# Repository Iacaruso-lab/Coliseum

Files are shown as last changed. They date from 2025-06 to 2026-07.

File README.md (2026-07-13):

# Coliseum

Hemispherical display to deliver simultaneous auditory and visual stimuli to head-fixed rodents. The device is composed by 15 slices.

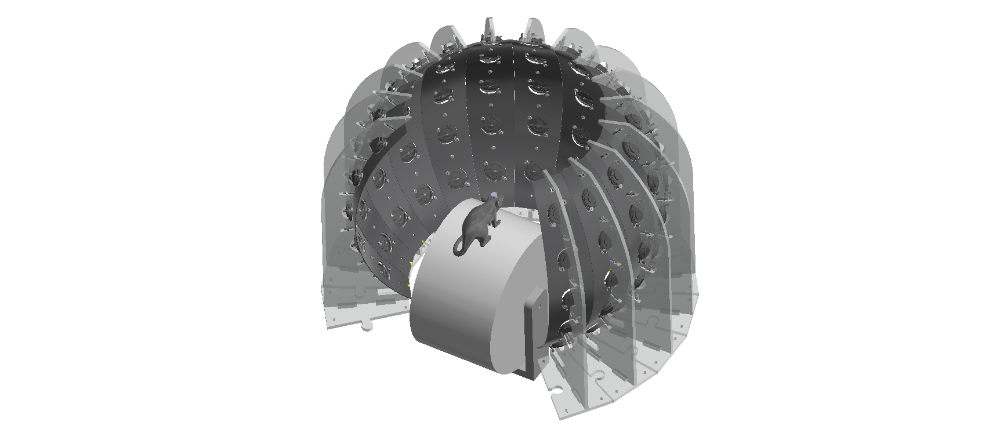
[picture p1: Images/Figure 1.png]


The device is designed to receive messages sent from the computer serial port, each message will contain digital information for each slide, basically which LED and which speaker goes into "ON state".

The audio signal is continuously generated from the PC and sent to all speakers but only the speakers set to ON will play the auditory signals.

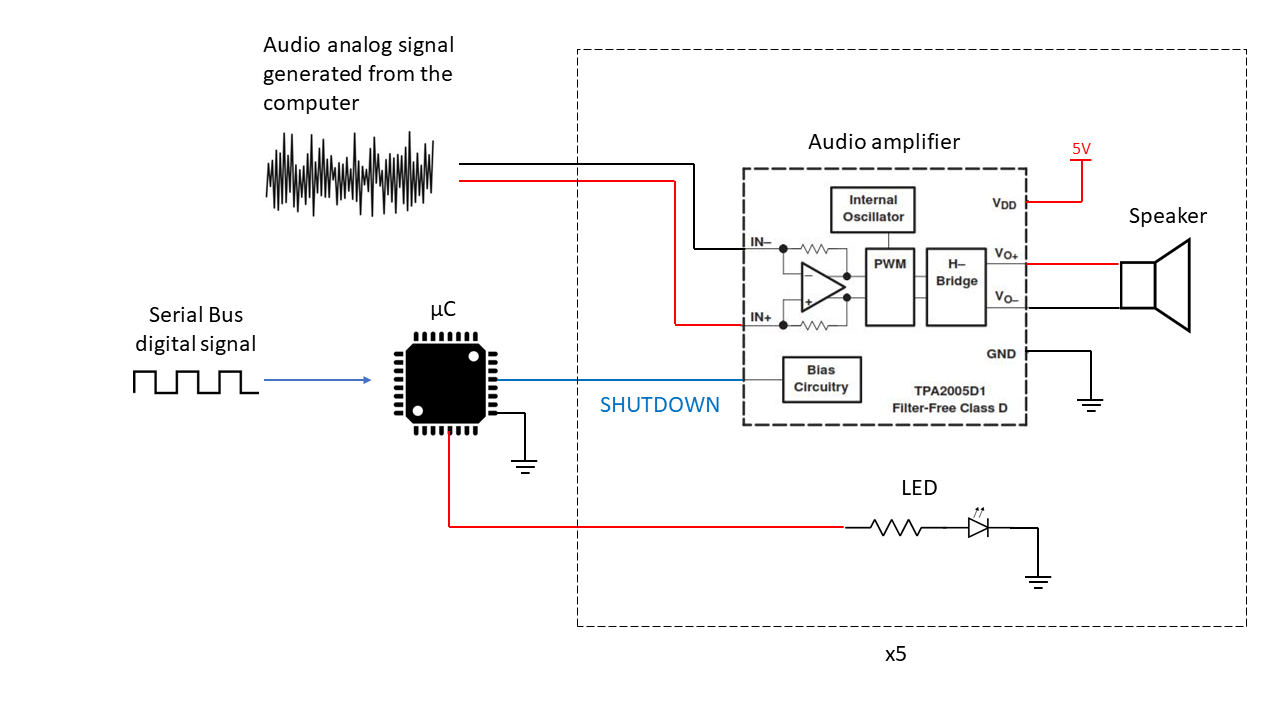
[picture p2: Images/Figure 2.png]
working principle


## Bill of materials

## Ordering the PCBs

First you need to create a customer account with [JLCPCB](https://jlcpcb.com/).

Then drag the gerber file from the [slice manufacturing files folder](Hardware/Manufacturing%20files/Slice%20PCB) into the instant quote file upload window.

Then select ***PCB quantity 15, PCB thickness 0.8 and color black.***

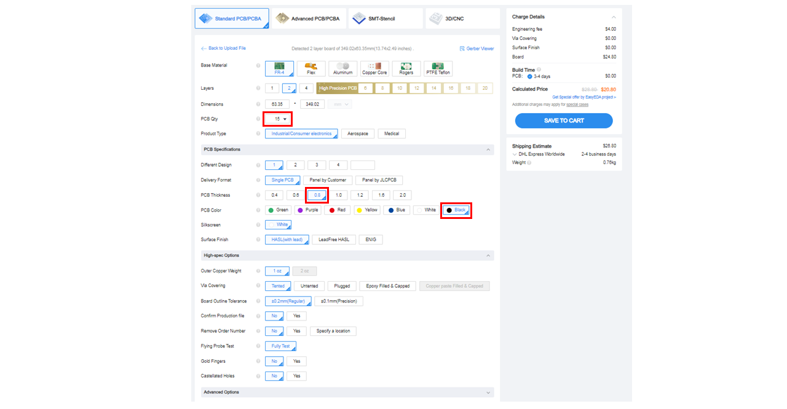
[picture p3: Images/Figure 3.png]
PCB order 1


Select PCB assembly and leave the selection of the top side for the assembly of the LEDs. Then select next.

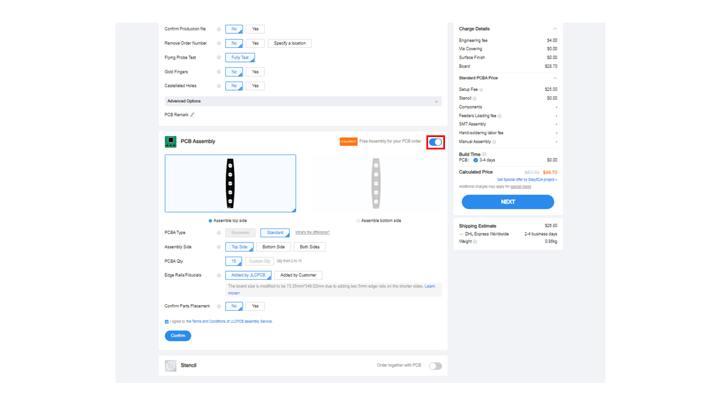
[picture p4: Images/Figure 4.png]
PCB order 2


Select next on the following step.

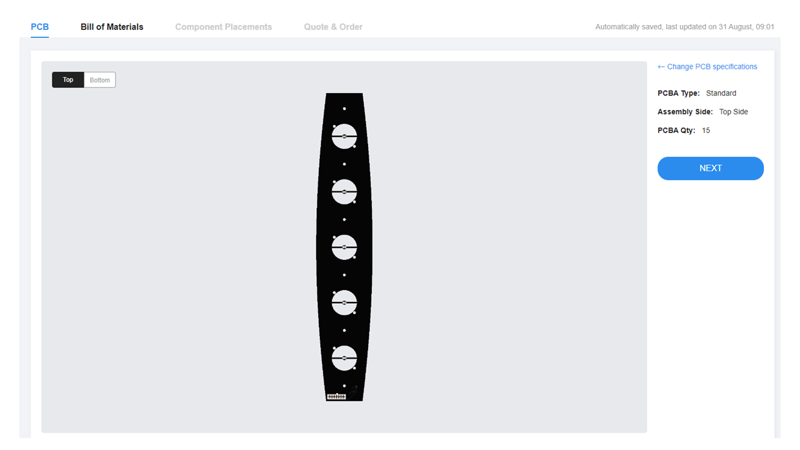
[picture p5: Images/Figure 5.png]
PCB order 3


After that wou are asked to upload the [BOM and Pick and Place files](Hardware/Manufacturing%20files/Slice%20PCB) then click on next.

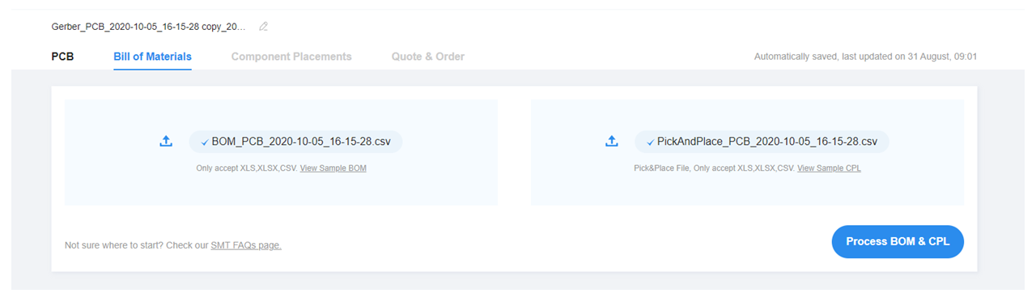
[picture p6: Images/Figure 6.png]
PCB order 4


On the following step you can select which components from the bill of materials you uploaded you want to be asembled on the board, when we ordered them there was no stock of the header, if there is, please ***unselect H1. Just leave selected the LEDs, coloured in red on the caption.***

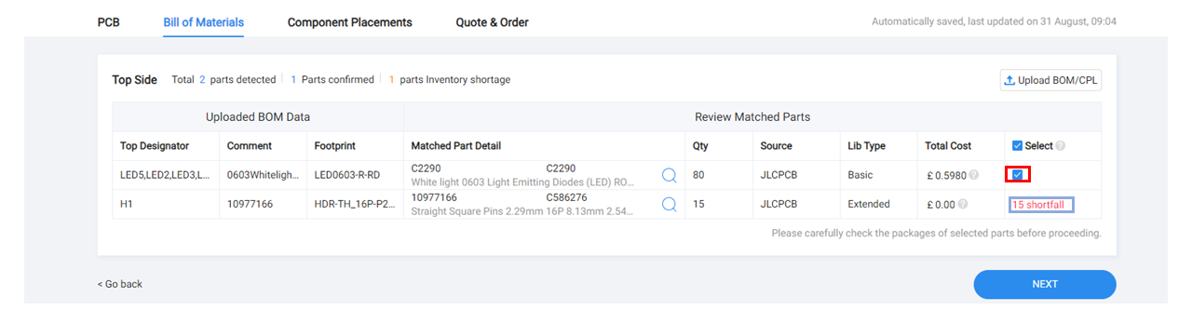
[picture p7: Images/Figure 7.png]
PCB order 5


After clicking on next you will get a message informing that your project has unselected parts, just click on ***"do not place"*** option.

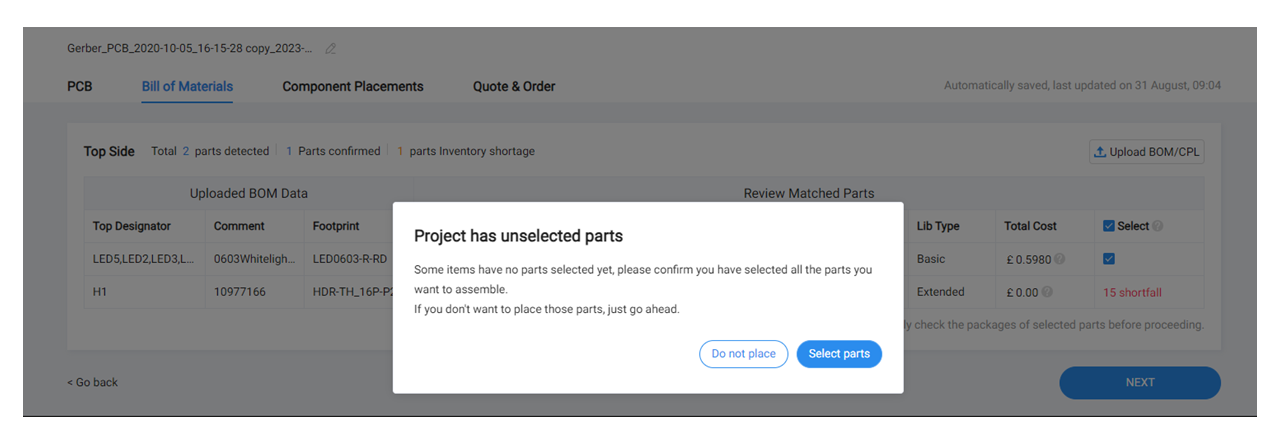
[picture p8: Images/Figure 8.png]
PCB order 6


On the render you ***should not see any part on top of the bottom header H1***, if you zoom in you will be able to see the LEDs in place where they will be once you receive the PCBs. Then you can click next.

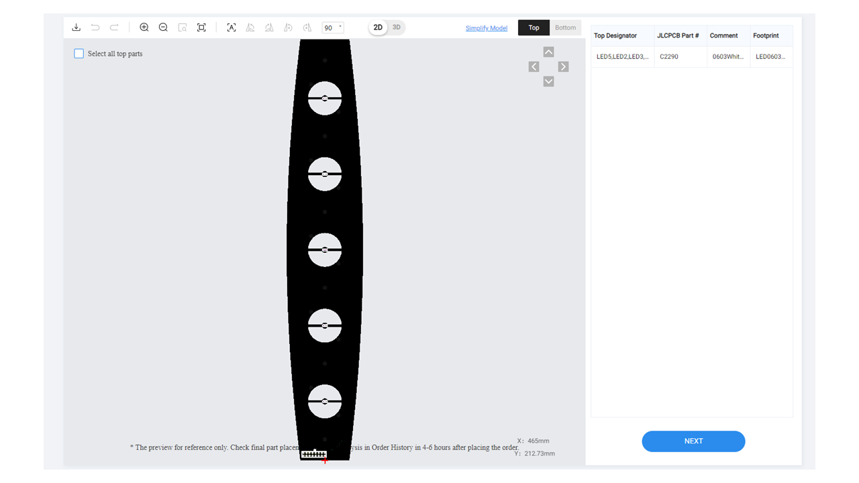
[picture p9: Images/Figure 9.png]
PCB order 7


On the last window you can just save the order for further payment.

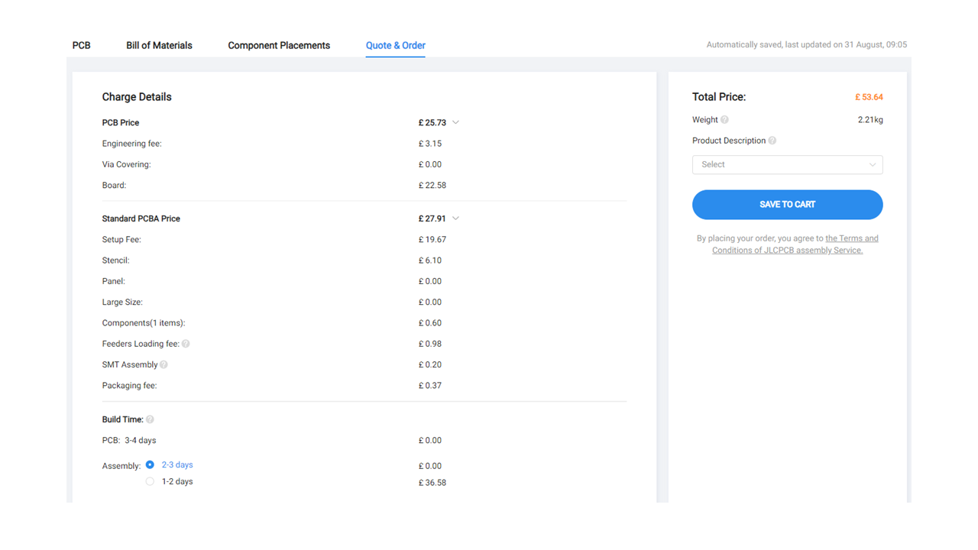
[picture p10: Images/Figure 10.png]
PCB order 8


The same steps have to be repeated for the [control board](Hardware/Manufacturing%20files/Control%20PCB/V7) manufacturing files, in that case ***the colour does not mater and can be the default greeen as well as the PCB thickness which can be the standard 1.6 mm***, the number of units is still 15.

## Assembly instructions

### Slice assembly

1- Laser cut the 15 slices acrylic structure. The ai. file "4 Slices Laser cutting file" contained in [the laser cut files folder](Hardware/Manufacturing%20files/Laser%20cut) has the 5 mm acrylic PMMA components needed for the main structure. Our file has been generated for a 600 mm x 300 mm laser cutter bed.

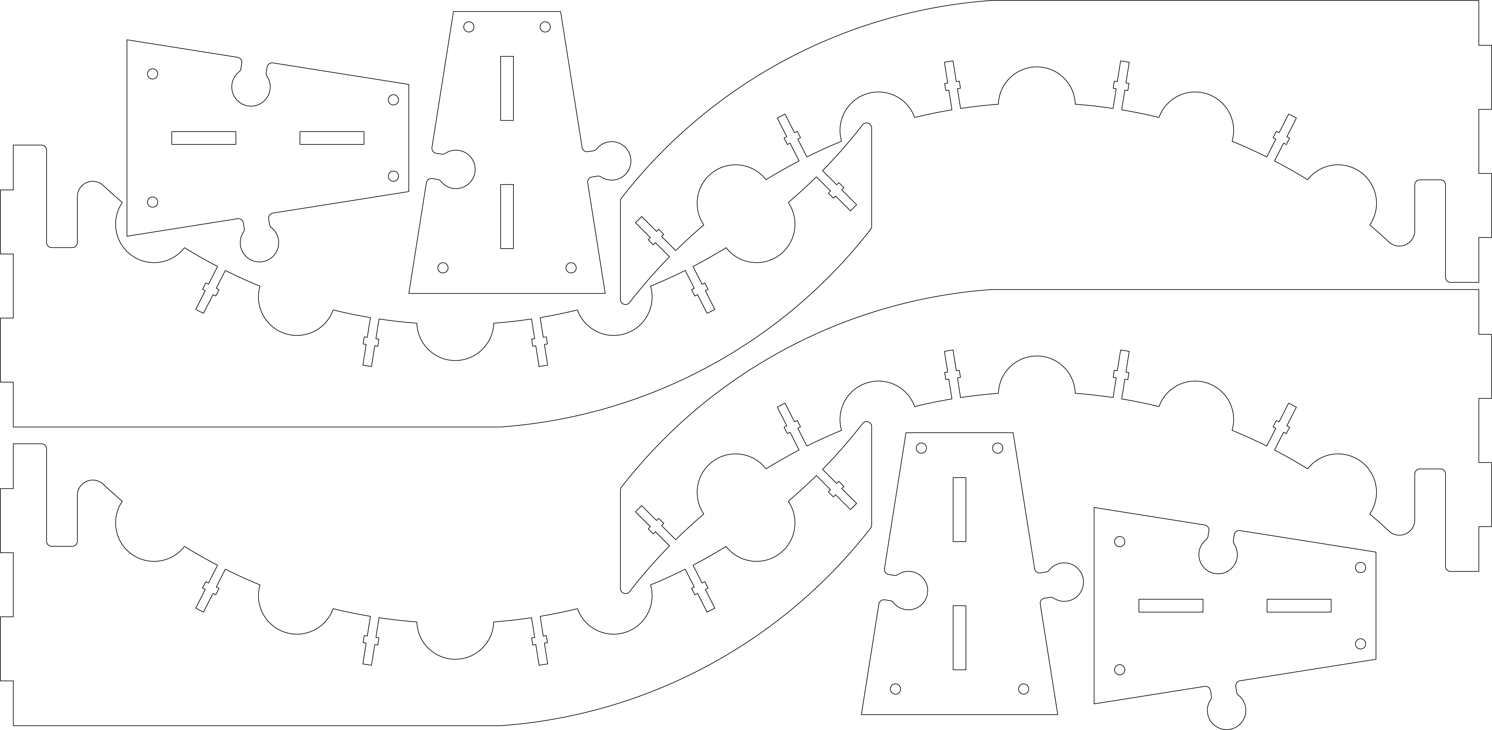
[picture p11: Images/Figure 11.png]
4 Slices (Laser cutting file)


Then both components of the acrylic structure are glued together, in our case we appyed the [Dymax UV curing glue](https://dymax.com/products/equipment/light-curing-equipment/spot-curing-systems) in the intersection of both parts, this step has to be repeated for each slide.

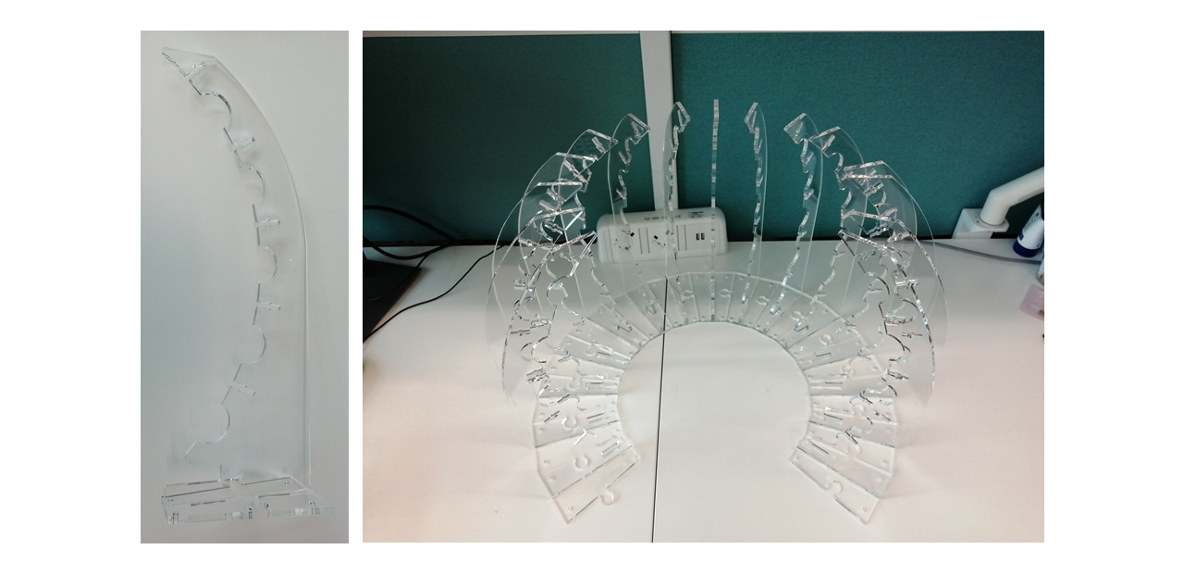
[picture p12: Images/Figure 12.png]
acrylic


The third component is the spacer which needs to be cut using 2 mm thick acrylic. You are going to need 150 spacers, a couple for each speaker. They will create the minimum space needed between the speaker membrane and the PCB avoiding the transfer of sound vibrations.

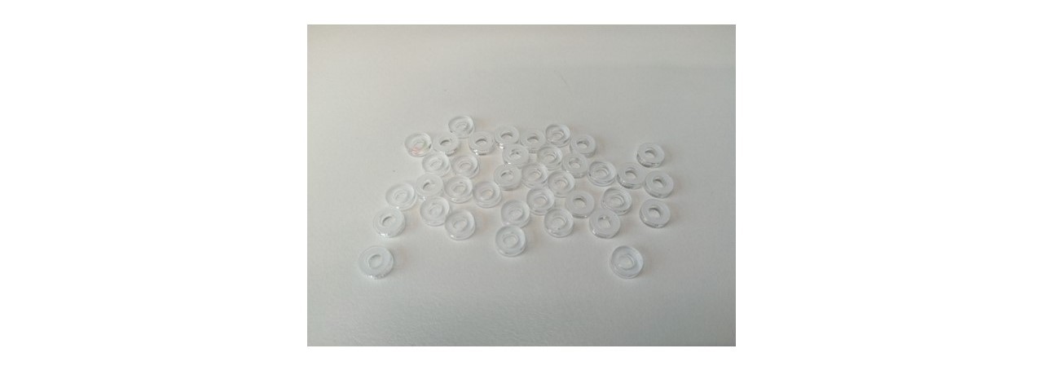
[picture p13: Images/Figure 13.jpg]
spacer


Each of the [speakers](https://www.digikey.co.uk/en/products/detail/visaton-gmbh-co-kg/K-28-WPC-BL-8-OHM/9842354) is attached with the PCB using 2 spacers, [2 M3 x 12 mm screws](https://www.amazon.co.uk/gp/product/B09Q5YYVQ2/ref=ppx_yo_dt_b_asin_title_o01_s00?ie=UTF8&psc=1) and two [M3 nuts](https://www.amazon.co.uk/TERF-Hexagon-Steel-Full-Nuts/dp/B09MDJHJTB/ref=sr_1_6?crid=2JZVZ1J4DZOUH&keywords=M3%2Bnuts&qid=1693322964&sprefix=m3%2Bnuts%2Caps%2C63&sr=8-6&th=1). Then all the Speakers are soldered using single core wire. The wire is cut at approximately 15 mm lengh and both sides stripped with a cable stripping tool.

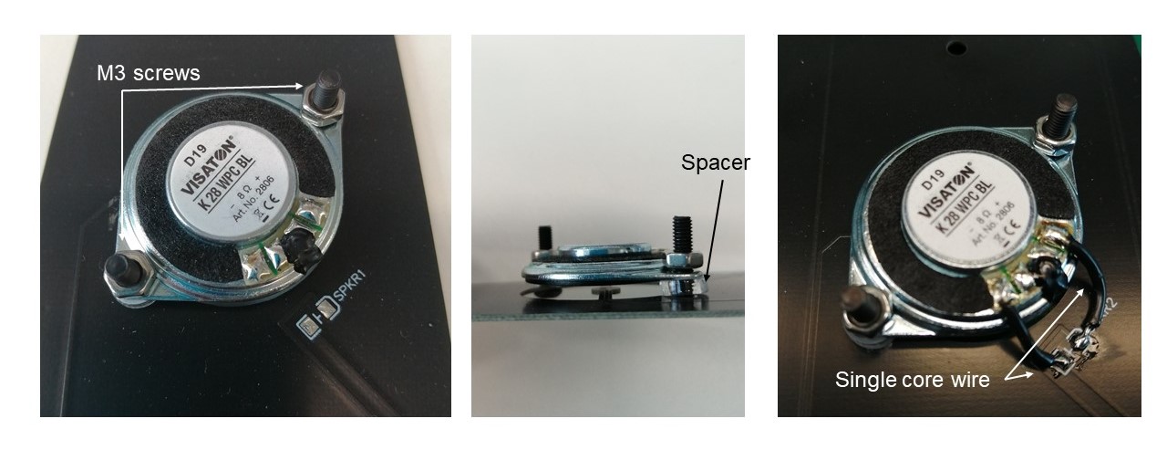
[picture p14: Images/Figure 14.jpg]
figures


The assembly of each slice PCB with its structure is done by using five M3 x 16 mm screws and five M3 nuts:

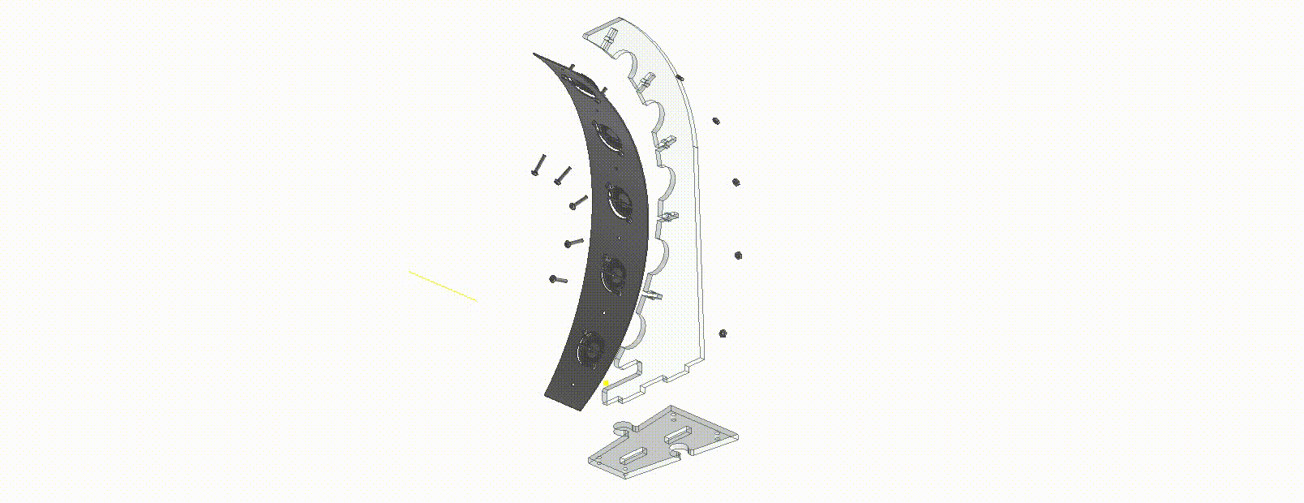
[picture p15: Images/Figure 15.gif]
Assembly


Once the slice is assembled, the last step is to bent the pins of the [8x2 female header](https://uk.farnell.com/samtec/esq-108-14-g-d/connector-rcpt-16pos-2row-2-54mm/dp/2779427) approximately 30 degrees using a ruler and solder the header into the back side of the PCB.

Slice assembly

Once you have repeated the process for all 15 slices you get this.

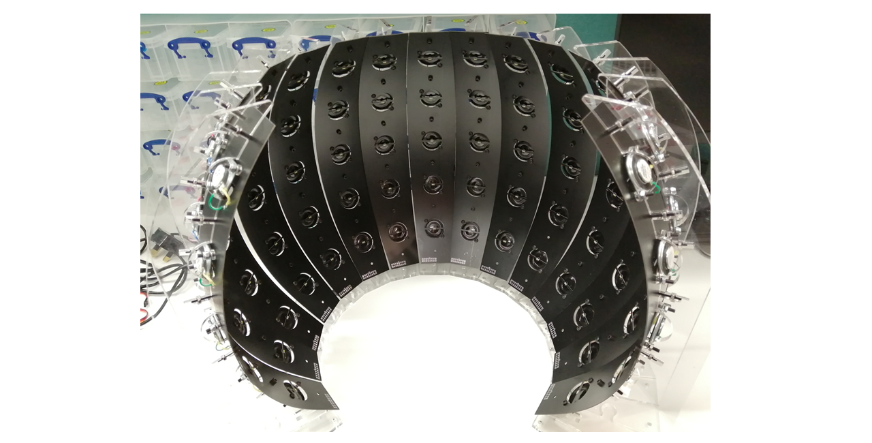
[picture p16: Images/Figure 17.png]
Coliseum assembled


### Control board assembly

If all components are in stock on [JLCPCB](https://jlcpcb.com/) the boards should arrive fully assembled and the only assembly step is the connection between its 90 degree connector and the slice connector.

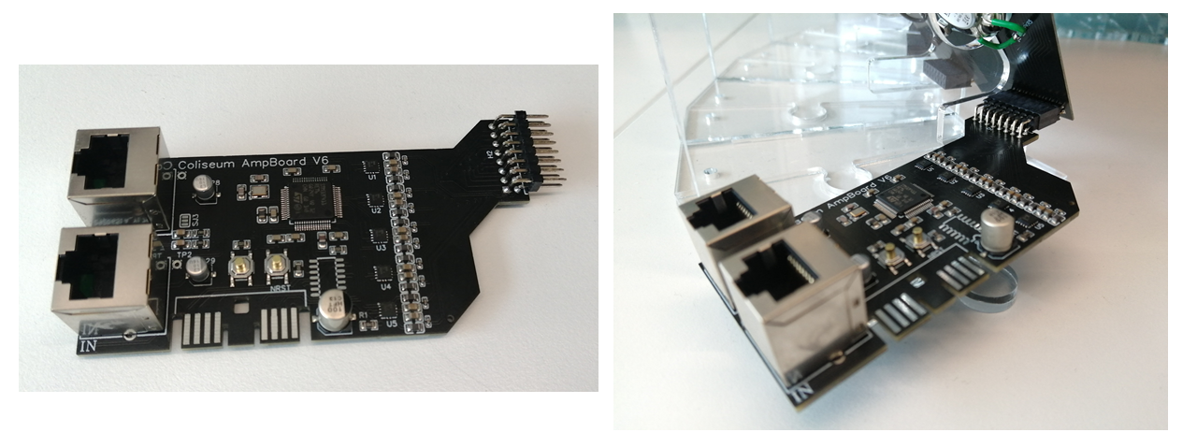
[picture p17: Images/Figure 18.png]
Coliseum board


### Programmer board assembly

The "georgeous STM32 programmer" board is composed by a custom PCB that is soldered on top of the [STM32 Nucleo-64 MCU Development Board NUCLEO-F410RB](https://uk.rs-online.com/web/p/microcontroller-development-tools/9173766?cm_mmc=UK-PPC-DS3A-_-google-_-3_UK_EN_Raspberry+Pi+%26+Arduino+%26+ROCK+%26+STEM+Education+%26+Development+Tools_Microcontroller+Development+Tools-_-STMicroelectronics+-+9173766+-+NUCLEO-_-stmicroelectronics+nucleo&matchtype=p&aud-2406926037817:kwd-327069370714&cq_src=google_ads&cq_cmp=12690202697&cq_term=stmicroelectronics%20nucleo&cq_plac=&cq_net=g&cq_plt=gp&gclsrc=aw.ds&gad_source=1&gad_campaignid=12690202697&gbraid=0AAAAADkeWNOcTAzA5nZgKzR7_I_gj5hWe&gclid=CjwKCAjwmdLSBhANEiwAkREMN9kaxucJEJcilK4NKpdcp2L4rGTd5La0k6RWjJVKPHo56LOtS3Y6xBoCotoQAvD_BwE) Serial to USB converter part that can snap and be separated from the rest of the development board.
Vcc, SWDIO, GND, SWCLK, NRST, RX and TX pins are soldered with a [Molex EdgeLock connector](https://www.mouser.co.uk/en/ProductDetail/Molex/200890-0106?qs=W0yvOO0ixfHAR9KO0O7TGQ%3D%3D) using a ribbon cable.

### If there is no stock of LEDs in JLCBPCB and you need to solder them my hand

The LEDs can be ordered to [RS components](https://uk.rs-online.com/web/p/leds/6541800).

You will have to check the polarity of each LED using a multimiter in the diode position. The position of the black and red probes will indicate the right polarity of the LED.

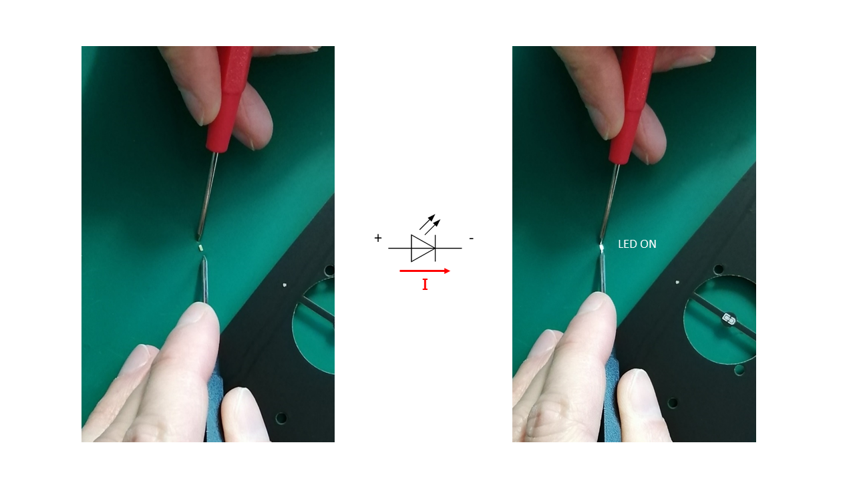
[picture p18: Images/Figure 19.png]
LED assembly 1


Twezzers are needed in order to solder the LEDs, The technique we used was add solder in one pad, then place the LED with the twezzers in contact with that pad while soldering the side where the solder was added. Once the LED is held in position the other pad of the LED can be soldered.

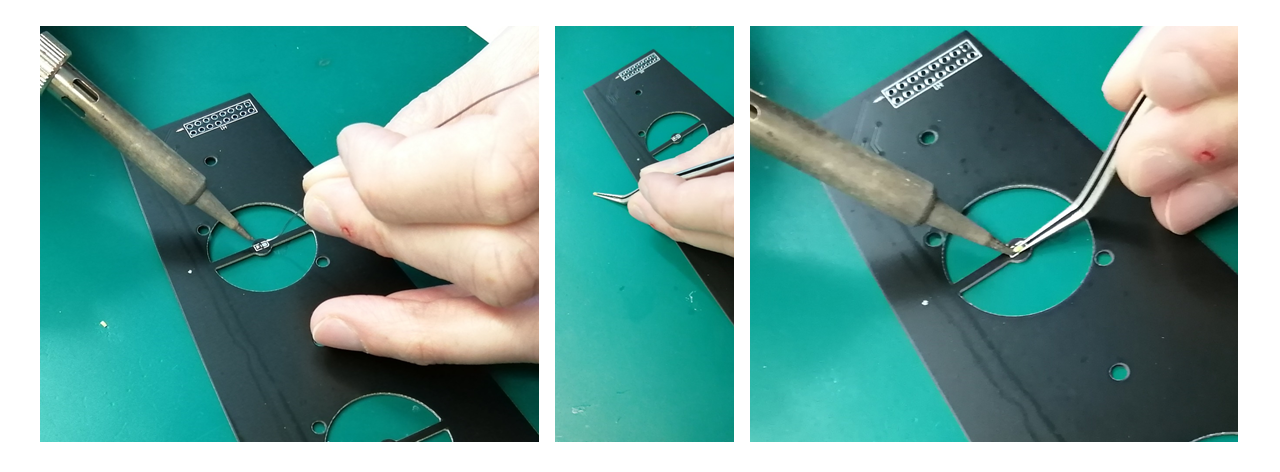
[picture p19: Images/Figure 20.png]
LED assembly 2


Then the polarity can be tested bt probing between the LED pin and GND pin.

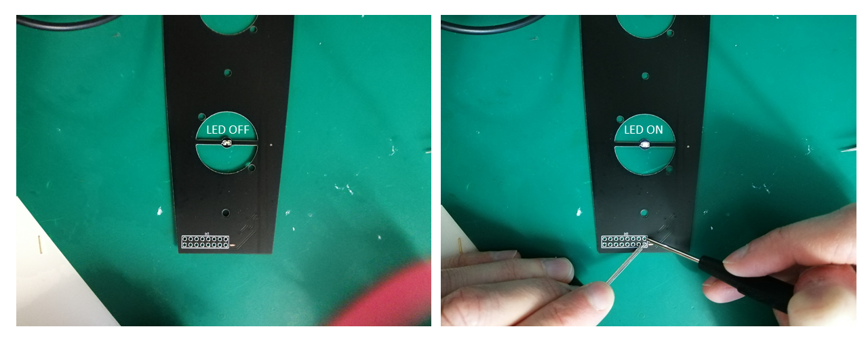
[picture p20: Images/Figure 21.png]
LED assembly 3


### Uploading the firmware

- Connect the board with the "georgeous STM32 programmer" (ST-LINK USB) cable.
- Connect the "georgeous STM32 programmer" to your computer using a mini USB cable.


- It will appear as a removable flash drive (e.g., NODE_Fxxx or Nucelo).
- Simply drag and drop  ["Colliseum_adjustablelight.NUCLEO_F411RE.bin"](https://github.com/Iacaruso-lab/Coliseum/blob/main/FirmWare/Colliseum_adjustablelight.NUCLEO_F411RE.bin) file onto the drive.
- The status LED will blink on your "georgeous STM32 programmer" board and rapidly flash.
- All slices are programmed with the same Firmware.

### Slices connection

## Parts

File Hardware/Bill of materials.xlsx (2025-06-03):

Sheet: Slice components
Component | Units (per slice) | Reference
Speaker | 5 | https://www.digikey.com/en/products/detail/visaton-gmbh-co-kg/K-28-WPC-BL-8-OHM/9842354
White LED | 5 | RS Components 654-1800
PCB holder stand | 1 | Manufacturing files\Laser cut
PCB holder base | 1 | Manufacturing files\Laser cut
Spacer | 10 | Manufacturing files\Laser cut
M3 screws 16 mm | 15 | RS Components 467-9818
M3 nuts | 15 | RS Components 527-230
Electronic board | 1
Ethernet patch cable | 2 | https://www.amazon.co.uk/gp/product/B00H8XNDTM/ref=ppx_yo_dt_b_asin_title_o03_s01?ie=UTF8&psc=1
2 row female Pin header | 1 | Farnell 2779427
Slice PCB
2 row male 90 deg pin header | 1 | Farnell 1593453

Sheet: Electric components
Component | Units | Reference
RS485 to USB adapter | 5 | https://www.amazon.co.uk/DSD-TECH-SH-U11F-Industrial-Application-White/dp/B083XSG1RG
BNC panel mount | 1 | RS Components 163-9548
3.3V 3A power supply | 1 | RS Components 413-677
Nylon cable gland | 1 | RS Components 882-9947
USB panel mount connector | 1
Ethernet panel mount connector | 1
Metal box | 1
Short USB Cable | 1
Jack panel mount connector | 1

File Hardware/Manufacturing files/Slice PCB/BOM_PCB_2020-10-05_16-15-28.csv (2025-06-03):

ID | Name | Designator | Footprint | Quantity | Manufacturer Part | Manufacturer | Supplier | Supplier Part | Price | Pins
1 | XL-1206QPC | SPKR1,SPKR2,SPKR3,SPKR4,SPKR5 | LED1206-RD | 5 |  |  |  |  |  | 2
2 | 10977166 | H1 | HDR-TH_16P-P2.54-V-M-R2-C8-S2.54 | 1 |  |  |  |  |  | 16
3 | 0603White light_C2290 | LED5,LED2,LED3,LED4,LED1 | LED0603-R-RD | 5 |  |  |  |  |  | 2

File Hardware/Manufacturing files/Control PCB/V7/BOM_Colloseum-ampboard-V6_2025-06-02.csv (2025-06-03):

ID | Name | Designator | Footprint | Quantity | Manufacturer Part | Manufacturer | Supplier | Supplier Part | Price | Pins
1 | HYCW82-RJ45-162B | U9,U6 | RJ45-TH_HYCW82-RJ45-162B | 2 | HYCW82-RJ45-162B | 华宇创 | LCSC | C3001545 | 0.295 | 10
2 | 100nF | C3,C4,C5,C6,C14,C16 | C0805 | 6 | CC0805KRX7R9BB104 | YAGEO(国巨) | LCSC | C49678 | 0.005 | 2
3 | 1uF | C7,C11,C18,C22,C26 | C0805 | 5 | CL21B105KBFNNNE | SAMSUNG(三星) | LCSC | C28323 | 0.009 | 2
4 | 2.2uF | C15 | C0805 | 1 | C2012X5R1V225KT000N | TDK | LCSC | C342807 | 0.099 | 2
5 | TestPin | TP2,TP1 | TESTPIN | 2 |  |  |  |  |  | 1
6 | PZ254-2-08-W-8.5 | H2 | HDR-TH_16P-P2.54-H-M-R2-C8-S2.54-W12.9-N | 1 |  | HCTL(华灿天禄) | LCSC | C2894988 | 0.227 | 16
7 | TS-1187A-C-G-A | NRST,BOOT | SW-SMD_4P-L5.1-W5.1-P3.70-LS6.4 | 2 | TS-1187A-C-G-B | XKB Connectivity(中国星坤) | LCSC | C318886 | 0.043 | 4
8 | Molex_EdgeLock_8 | P1 | MOLEX_EDGE_LOCK_8 | 1 |  |  | RS-Online | 174-2022 |  | 8
9 | 10uF | C28,C29 | CAP-SMD_BD4.0-L4.3-W4.3-LS5.1-FD | 2 |  | lelon(立隆) | LCSC | C249724 | 0.054 | 2
10 | 220nF | C8,C12,C19,C23,C31,C32,C34 | C0805 | 7 |  | SAMSUNG(三星) | LCSC | C5378 | 0.011 | 2
11 | 100nF | C9,C10,C13,C17,C20,C21,C24,C25,C35,C36 | C0402 | 10 |  | SAMSUNG(三星) | LCSC | C307331 | 0.005 | 2
12 | 22uH | L3,L4,L5,L6,L7,L8,L9,L10,L11,L12 | L0805 | 10 | SDFL2012T220KTF | Sunlord(顺络) | LCSC | C32375 |  | 2
13 | 150kΩ | R7,R8 | R0805 | 2 |  | RESI(开步睿思） | LCSC | C328382 | 0.011 | 2
14 | SOLDERJUMPER_2WAYS | SJ3 | SJ_3 | 1 |  |  |  |  |  | 3
15 | TPA2005D1DRBR_C88033 | U1,U2,U3,U4,U5 | SON-8_L3.0-W3.0-P0.65-BL-EP | 5 |  | TI(德州仪器) | LCSC | C88033 | 0.998 | 9
16 | 20pF | C1,C2 | C0805 | 2 | CL21C200JBANNNC | SAMSUNG(三星) | LCSC | C1798 | 0.014 | 2
17 | 100uF | C27 | CAP-SMD_BD6.3-L6.6-W6.6-FD | 1 | EEEFTH101XAP | PANASONIC(松下) | LCSC | C165974 | 0.364 | 2
18 | 10uH | L1 | L0805 | 1 | SDFL2012S100KTF | Sunlord(顺络) | LCSC | C1046 |  | 2
19 | 240 | R1 | R0805 | 1 | 0805W8F2400T5E | UNI-ROYAL(厚声) | LCSC | C17572 | 0.002 | 2
20 | 12K | R3,R4,R5 | R0805 | 3 | 0805W8F1202T5E | UNI-ROYAL(厚声) | LCSC | C17444 | 0.002 | 2
21 | 25MHz | X1 | OSC-SMD_4P-L3.2-W2.5-BL | 1 | X322525MOB4SI | YXC(扬兴晶振) | LCSC | C9006 | 0.068 | 4
22 | STM32F411RET6 | U7 | LQFP-64_L10.0-W10.0-P0.50-LS12.0-BL | 1 | STM32F411RET6 | ST(意法半导体) | LCSC | C94355 | 2.688 | 64
23 | AD8402ARZ1 | U8 | SOIC-14_L8.7-W3.9-P1.27-LS6.0-TL | 1 | AD8402ARZ1 | ADI(亚德诺)/LINEAR(凌特) | LCSC | C386279 | 11.632 | 14

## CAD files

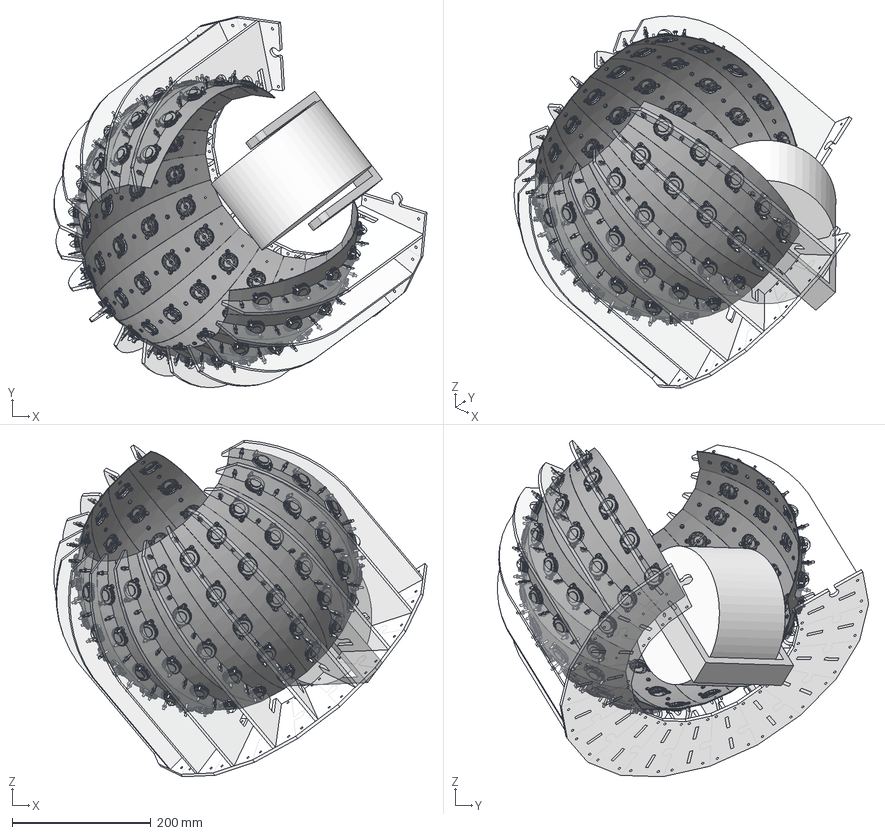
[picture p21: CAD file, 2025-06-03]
Hardware/STEP files/Assembly.stp
538.1 x 535.8 x 485.4 mm
Base x 15
PCB holder x 15
Spherical PCB 2 x 15
SMD LED x 75
AS 1427 - M3 x 16(4) x 75
AS 1427 - M3 x 12(4) x 150
AS 1474 - M3(1) x 225
K 28 WP BL 170907 x 75
Speaker spacer x 150
Treadmill holder

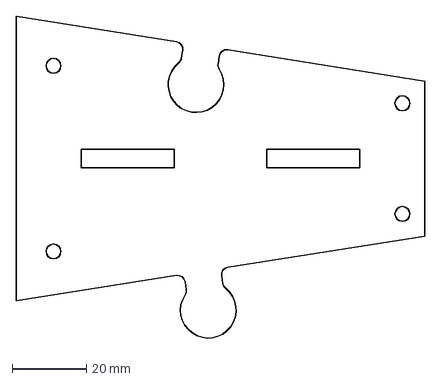
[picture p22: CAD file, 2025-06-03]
Hardware/Manufacturing files/Laser cut/PCB holder base.dxf
110.0 x 87.6 mm

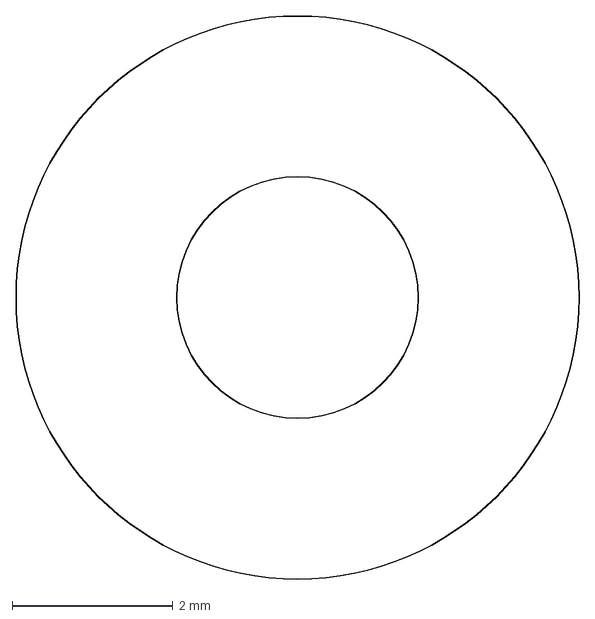
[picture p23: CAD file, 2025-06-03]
Hardware/Manufacturing files/Laser cut/Spacer.dxf
7.00 x 7.00 mm

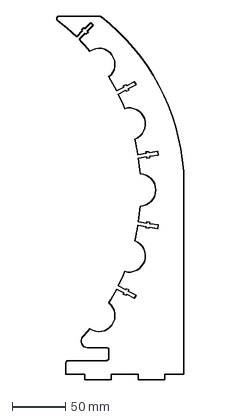
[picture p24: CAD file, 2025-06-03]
Hardware/Manufacturing files/Laser cut/PCB holder stand.dxf
118.8 x 340.0 mm

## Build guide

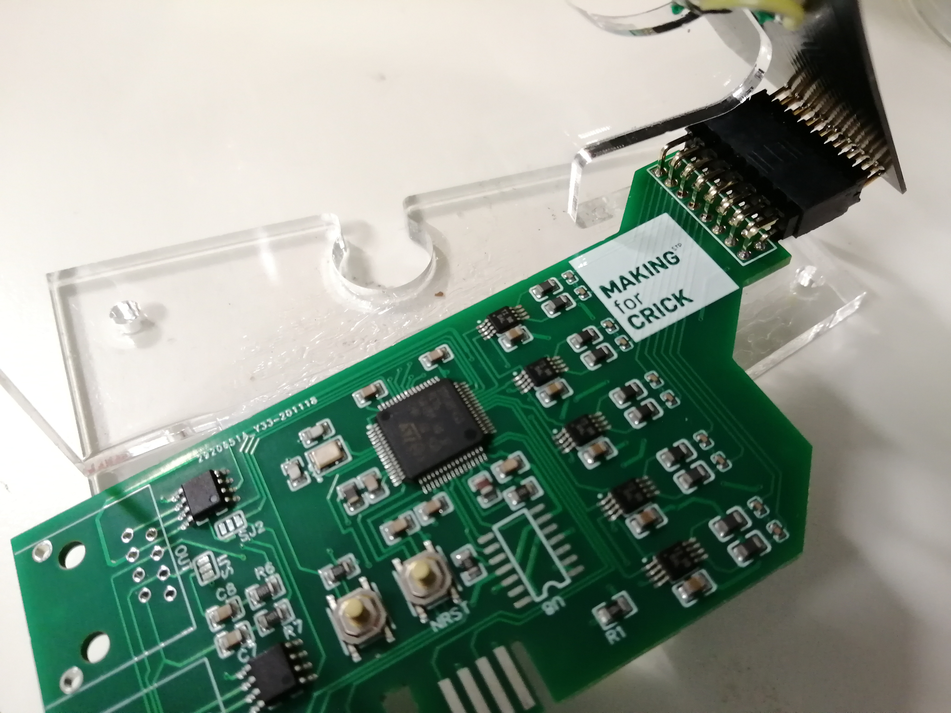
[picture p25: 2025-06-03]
Hardware/Assembly pictures/IMG_20210114_172149.jpg

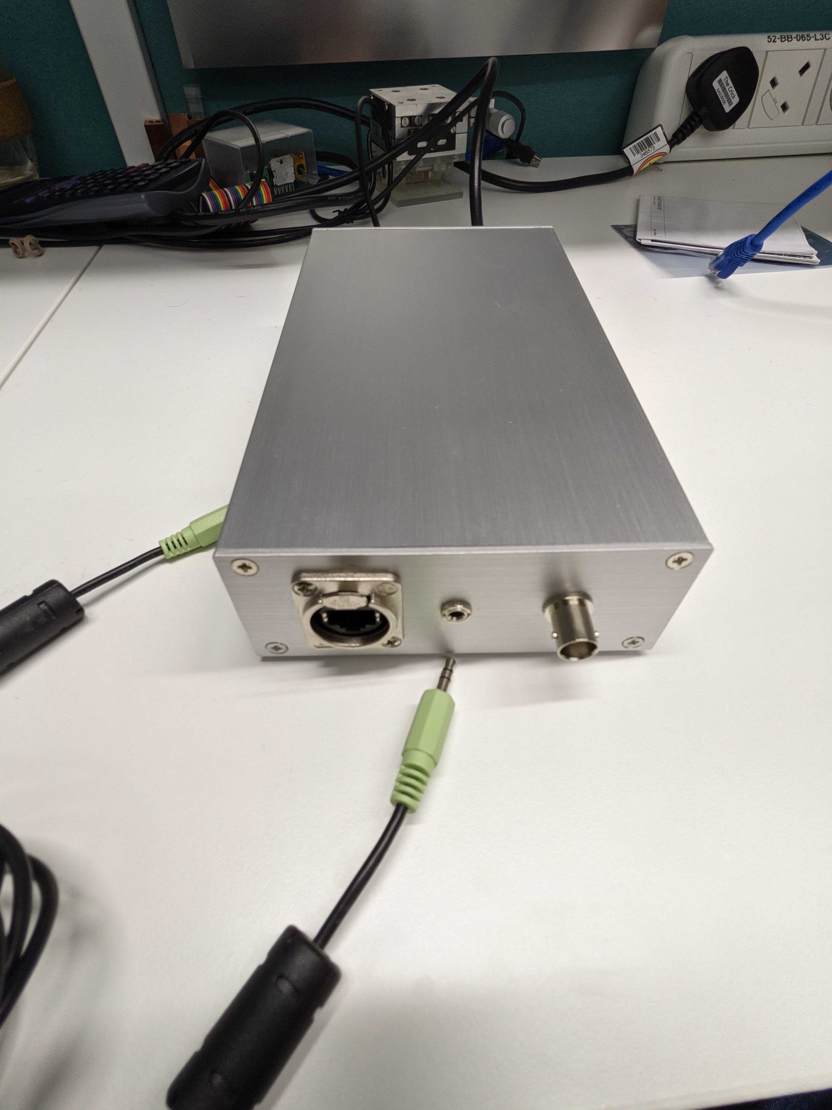
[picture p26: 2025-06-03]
Hardware/Assembly pictures/PXL_20210320_181853031.MP.jpg

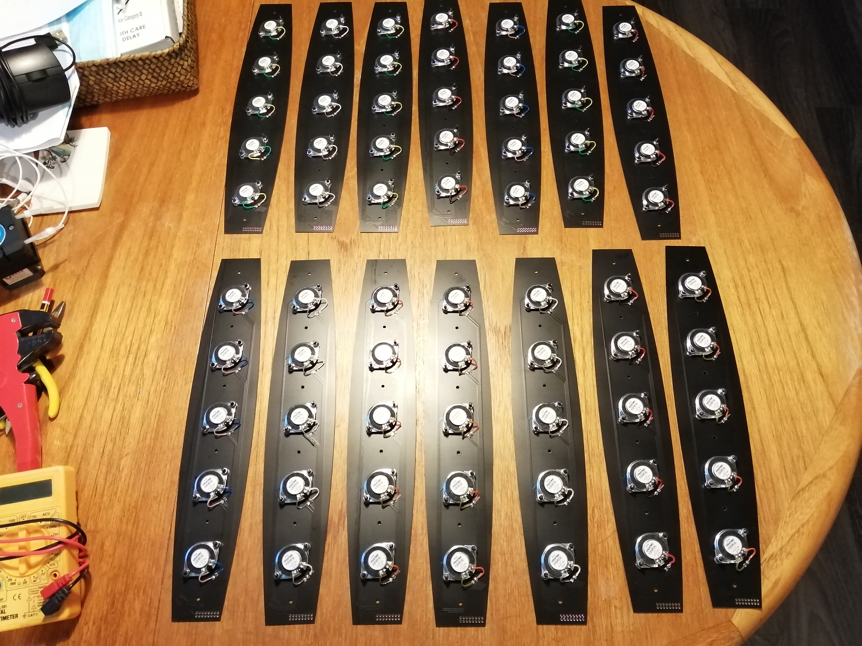
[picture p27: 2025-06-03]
Hardware/Assembly pictures/IMG_20210112_162315.jpg

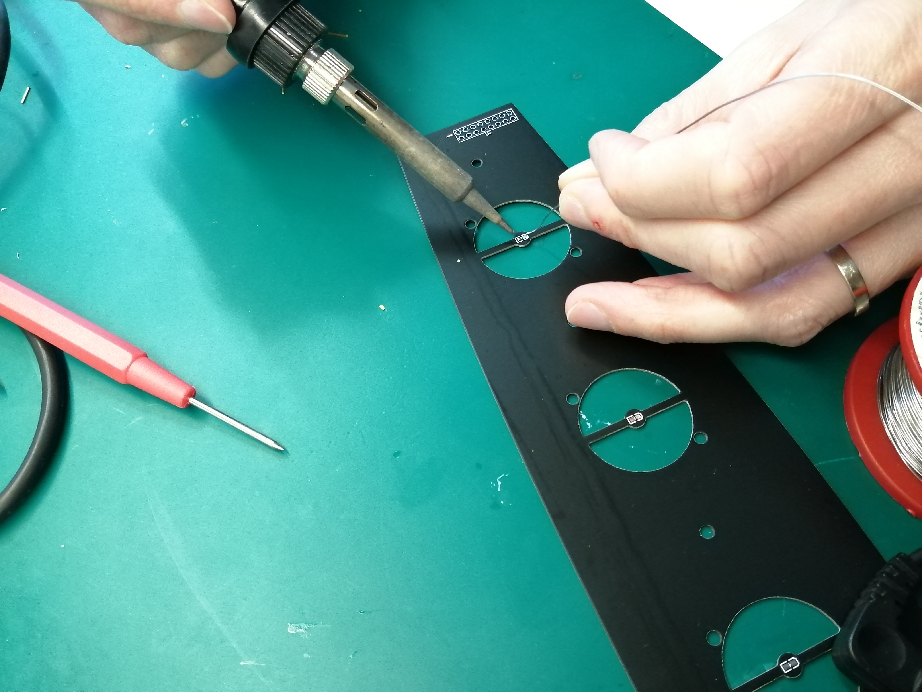
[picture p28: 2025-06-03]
Hardware/Assembly pictures/IMG_20210120_133439.jpg

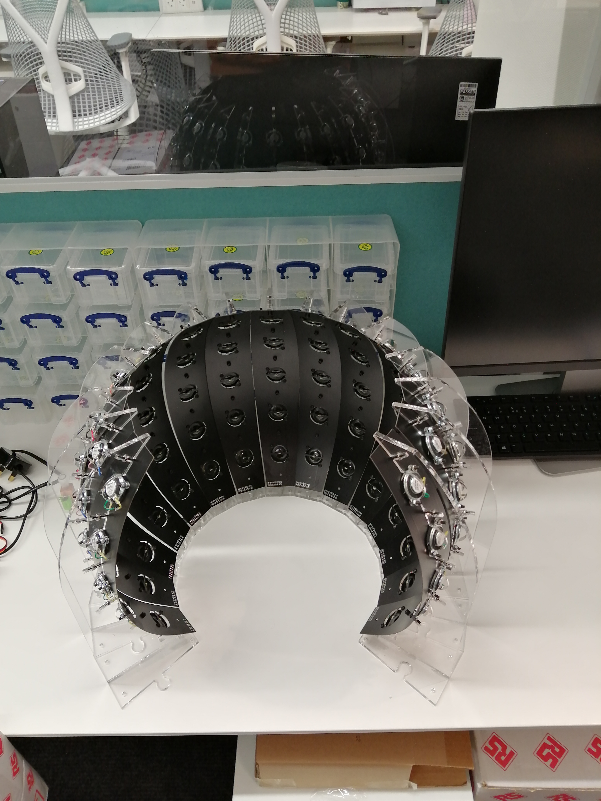
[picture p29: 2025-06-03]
Hardware/Assembly pictures/IMG_20210114_190305.jpg

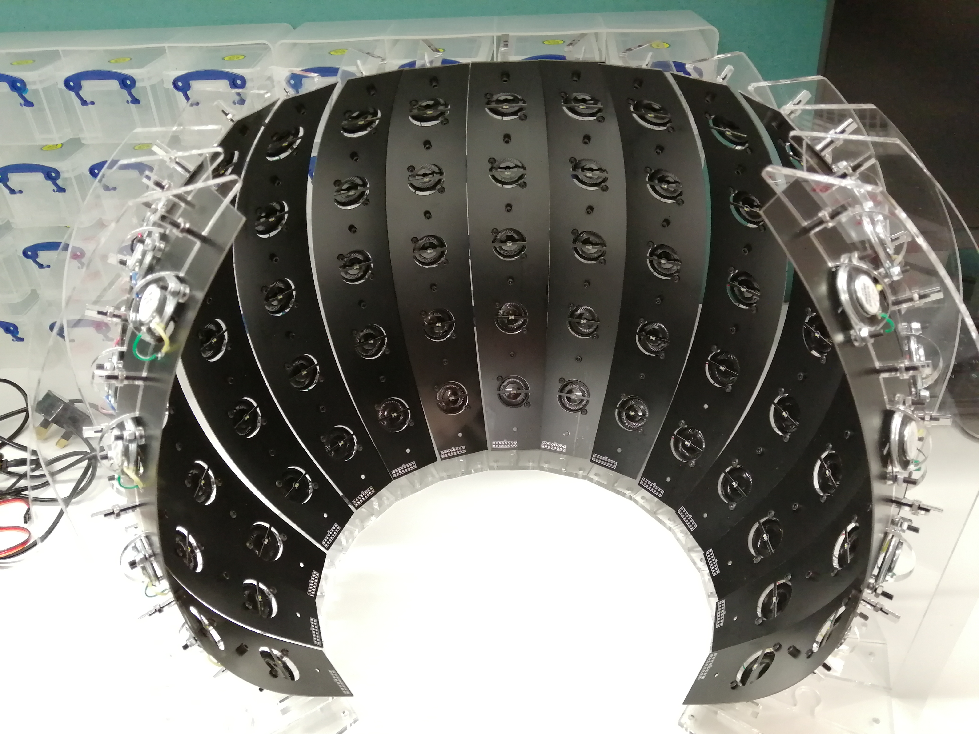
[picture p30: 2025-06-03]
Hardware/Assembly pictures/IMG_20210114_190258.jpg

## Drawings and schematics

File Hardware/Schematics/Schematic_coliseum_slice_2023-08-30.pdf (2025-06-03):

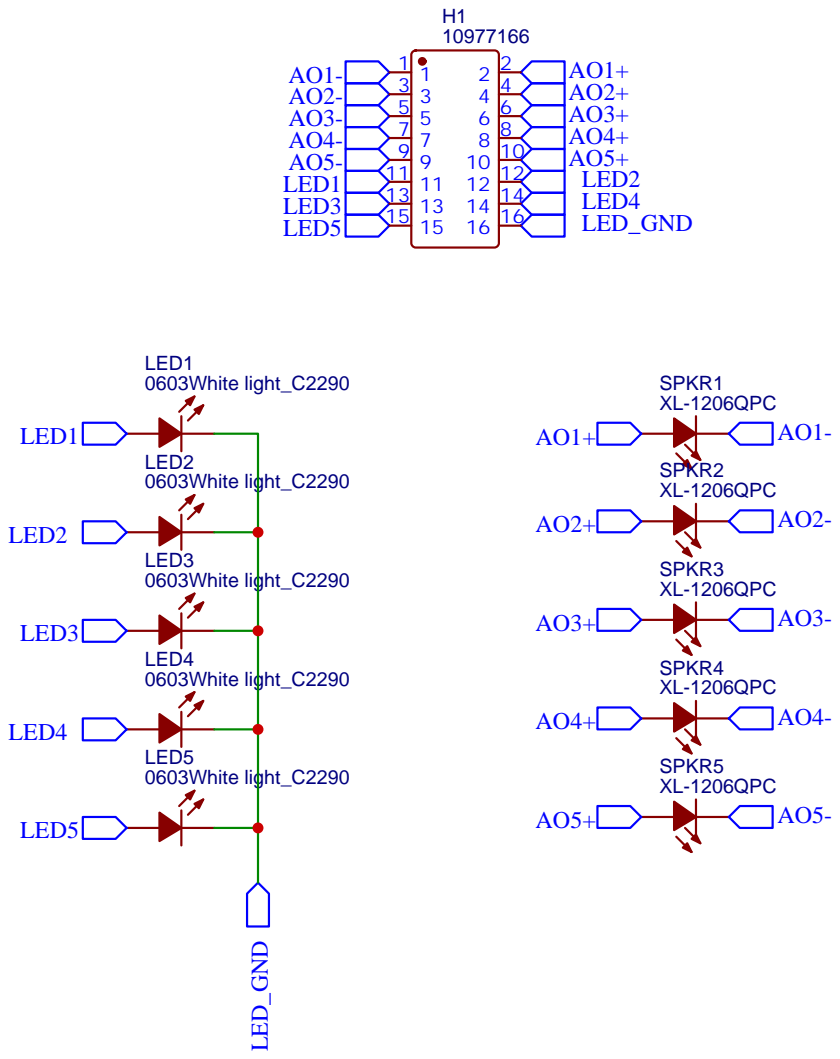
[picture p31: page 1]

Company: The MAking STP/ The Crick

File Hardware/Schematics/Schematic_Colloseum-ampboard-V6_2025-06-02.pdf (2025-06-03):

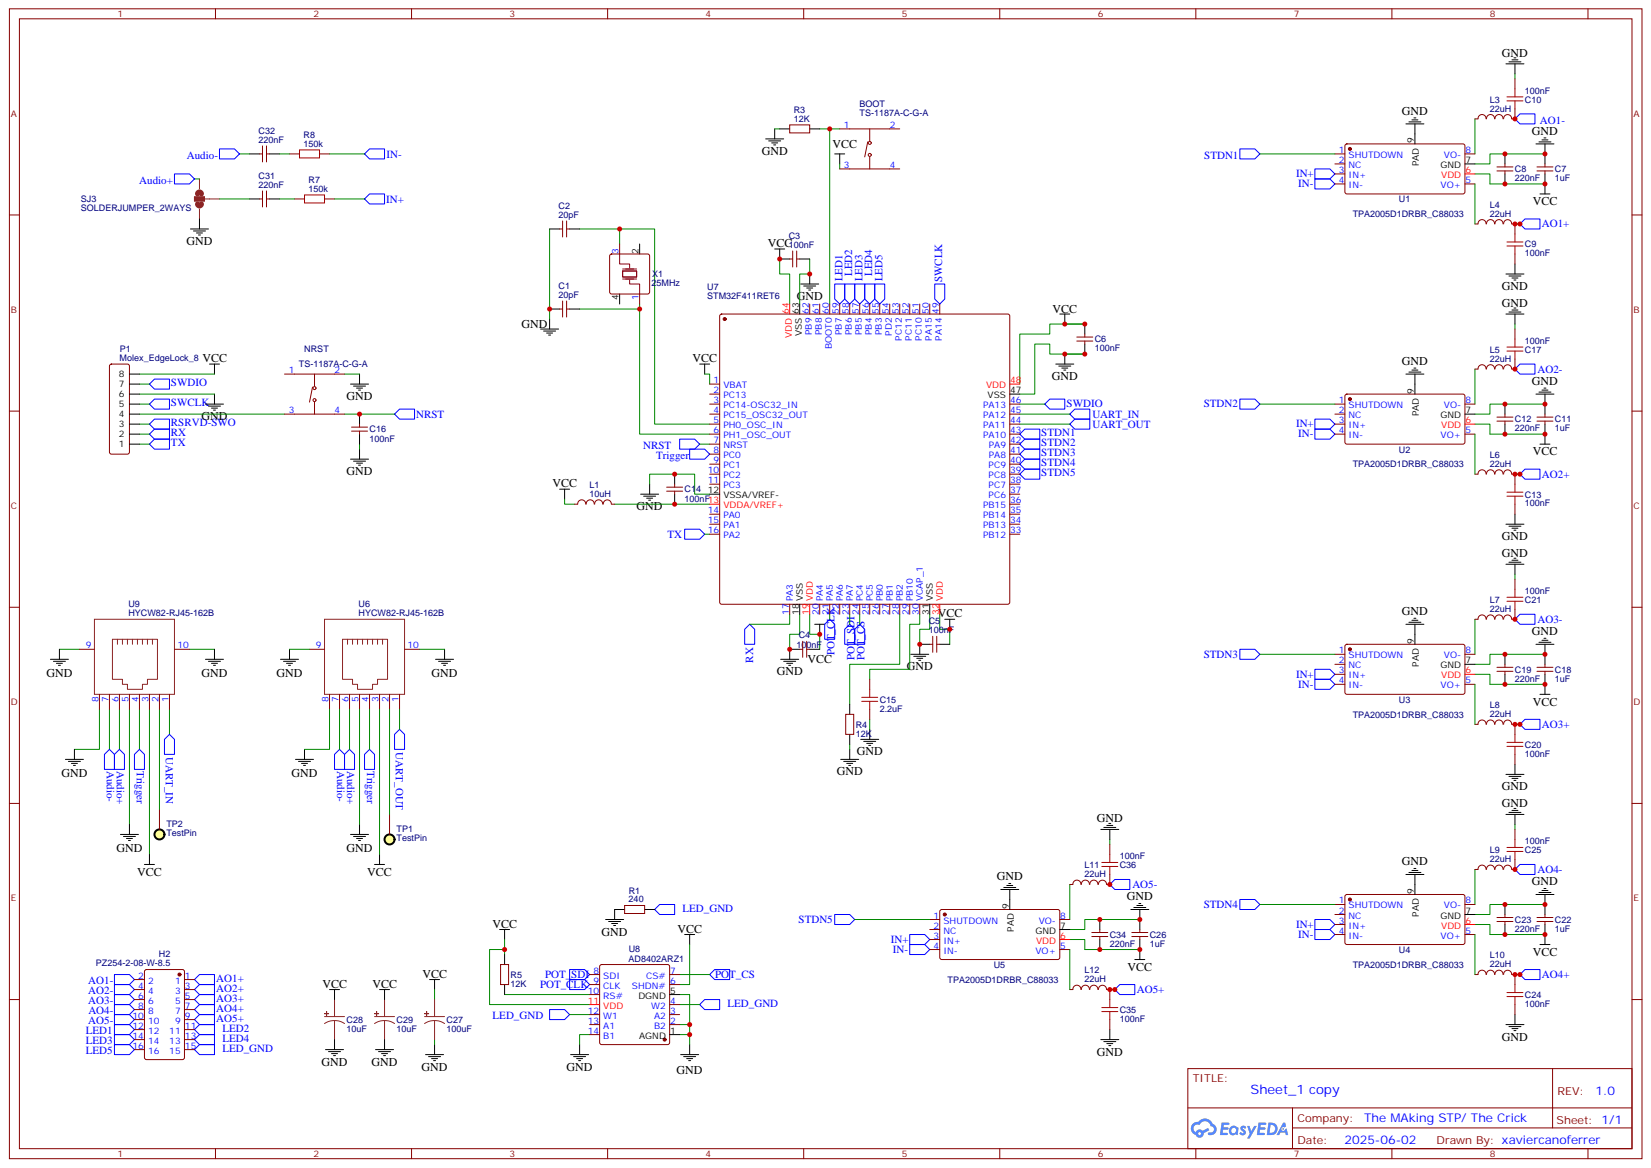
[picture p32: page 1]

Company: The MAking STP/ The Crick

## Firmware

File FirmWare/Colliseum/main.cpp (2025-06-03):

#include "mbed.h"
#include "SWSPI.h"

SWSPI spi(PA_7, PA_6, PA_5); // mosi, miso, sclk
DigitalOut CS(PC_4);

DigitalOut led1(PB_7);
DigitalOut led2(PB_6);
DigitalOut led3(PB_5);
DigitalOut led4(PB_4);
DigitalOut led5(PB_3);


DigitalOut spkr1(PA_10);
DigitalOut spkr2(PA_9);
DigitalOut spkr3(PA_8);
DigitalOut spkr4(PC_9);
DigitalOut spkr5(PC_8);

int intensity=0;
char read_byte,cmnd_byte,cmnd_led,cmnd_spkr;

Serial rs485(PA_11, PA_12);
Serial pc(PA_2, PA_3);  // tx, rx
 

 
int main() {
    CS=1;
    spi.format(10,0);
    spi.frequency(1000000);
    
    pc.baud(115200);
    rs485.baud(115200);
    pc.printf("Hello there! Let's rave! \n\r");
    while(1) {

     read_byte= rs485.getc();
    
        if(read_byte==0xFF){
            cmnd_byte=rs485.getc();
            cmnd_led= cmnd_byte & 0x0F;
            cmnd_spkr= cmnd_byte>>4;
            
            rs485.putc(0xFF);
            //pc.printf("Initialisation byte received. Command:  0x%.2X\n\r",cmnd_byte);
            //pc.printf("SPKR %d",cmnd_spkr);
            //pc.printf("    LED: %d\n\r",cmnd_led);
            
            }
        else if (read_byte==0xFE){
            intensity=rs485.getc();
            rs485.putc(0xFE);
            rs485.putc(intensity);
            CS=0;
            spi.write(0b0000000000|intensity); //only using one POT channel, otherwise also send 0b0100000000 OR intensity
            CS=1;
            //pc.printf("I just set the intensity to %d\n\r", intensity);
            }
        else {
            rs485.putc(read_byte);
            cmnd_byte=0;
            //pc.printf("another one bytes the dust! 0x%.2X\n\r",read_byte);
            }
    

    
        switch(cmnd_led){
            case 1:
               led1=1;
               led2=0;
               led3=0;
               led4=0;
               led5=0; 
               break;
             case 2:
               led1=0;
               led2=1;
               led3=0;
               led4=0;
               led5=0; 
               break;
            case 3:
               led1=0;
               led2=0;
               led3=1;
               led4=0;
               led5=0; 
               break;
            case 4:
               led1=0;
               led2=0;
               led3=0;
               led4=1;
               led5=0; 
               break;
            case 5:
               led1=0;
               led2=0;
               led3=0;
               led4=0;
               led5=1; 
               break;   
            default:
               led1=0;
               led2=0;
               led3=0;
               led4=0;
               led5=0; 
               //pc.printf("wrong LED number \n\r");
               
               break;
           }    
     
         switch(cmnd_spkr){
            case 1:
               spkr1=1;
               spkr2=0;
               spkr3=0;
               spkr4=0;
               spkr5=0; 
               break;
             case 2:
               spkr1=0;
               spkr2=1;
               spkr3=0;
               spkr4=0;
               spkr5=0; 
               break;
            case 3:
               spkr1=0;
               spkr2=0;
               spkr3=1;
               spkr4=0;
               spkr5=0; 
               break;
            case 4:
               spkr1=0;
               spkr2=0;
               spkr3=0;
               spkr4=1;
               spkr5=0; 
               break;
            case 5:
               spkr1=0;
               spkr2=0;
               spkr3=0;
               spkr4=0;
               spkr5=1; 
               break;   
            default:
               spkr1=0;
               spkr2=0;
               spkr3=0;
               spkr4=0;
               spkr5=0; 
               //pc.printf("wrong SPEAKER number \n\r");
               
               break;
       }            
              

      
        
     //pc.printf("\n\r");    
        
    }
}
